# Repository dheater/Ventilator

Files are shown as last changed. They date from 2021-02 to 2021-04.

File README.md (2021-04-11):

# RespiraWorks Open Source Ventilator












This is a common repository for all hardware and software components of the RespiraWorks open source ventilator.

**If you intend to contribute, please read our [wiki](https://github.com/RespiraWorks/Ventilator/wiki).**

[RespiraWorks](https://respira.works/) is a 501(c)(3) non-profit organization with over 200 contributors worldwide
working to rapidly design a low-cost and [open-source](open_source.md) ventilator for communities underserved by the
global supply chain. Our objective is to provide the know-how and technology to enable others to manufacture these
systems and put them in the hands of those who need them most.

| Most recent rendering  | Assembled v0.3 prototype |
|:---:|:---:|
|  |  |

## Design Goals

We are dedicated to making this ventilator:
* [fully open source (software and hardware)](open_source.md)
* affordable (materials cost under US$2000)
* fully featured for extended clinical use through weaning and recovery
* vetted and filing-ready for regulatory review around the world
* optimized bill of materials to account for constrained (medical) supply chains
* designed for long-term clinical use beyond the pandemic

Most low-cost ventilator designs that have emerged in light of the COVID-19 crisis tackle the 'bridge' problem —
keeping a patient alive for 6-8 hours of closely monitored care until they can be transitioned to a full
ventilator. We are designing that full ventilator, a highly valued medical device critical to care beyond the
current crisis.

Our design shall provide essential features such as an intuitive, localized user interface, adaptive pressure- and
volume-based operating modes, fine control of oxygen concentration, High Flow Nasal Cannula and other advanced features.
What sets us apart from other similarly ambitious projects is our dedication to being fully open source. This repository
embodies that promise.

We are targeting middle- and low-income parts of the world that will deal with COVID-19 for longer, with less access
to healthcare, and a larger deficit of medical devices. We aim to deliver a design which meets the same operational
rigors of current commercial ventilators, while addressing the high barrier to entry for such devices.

The maturity of our design is attested to by our collaboration with [Foundry-M](http://www.foundrym.in/), a startup
in Visakhapatnam, India. We are working closely with our colleagues in India to adapt this design to their local
manufacturing capabilities and regulatory needs.

If you can lend your skills towards achieving this goal, please contact us at
[join-us@respira.works](mailto:join-us@respira.works?subject=[GitHub]%20Join%20request). A list of roles we are looking
to fill is also on our [website](https://respira.works/join-us).

## DISCLAIMERS

**This is an incomplete, as yet untested design that is not yet intended to be used on patients.**

**The repository contains live documents. There may be incomplete or contradictory information about various aspects
of the design. Components may or may not connect and integrate as intended. Contents may also be out of date. If you
decide to buy or build anything, do so at your own risk.**

## Repository Structure

* [**System Requirements**](https://respiraworks.github.io/Ventilator/system/system_requirements.html) -
  describes the requirement architecture, hierarchy, and process. Links to the releases of our system requirements,
  hardware specifications, and software requirements
* [**System Design**](design) -
  describes the functional implementation and design theory of the system
* [**Manufacturing Design**](manufacturing) - describes the physical design of the ventilator and its components.
  Includes CAD models and notes on the manufacturing process
* [**Main Circuit Board**](pcb) - design, materials, assembly instructions for the ventilator main circuit board
* [**Software**](software) - Source code for cycle controller and user interface, debug tools, test scripts, and test data
* [**Quality Assurance**](quality-assurance) - quality assurance strategy, testing plans, data

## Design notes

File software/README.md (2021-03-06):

# Ventilator Software

This directory contains the source code for the ventilator software, test code, sample data and debug utilities.

**DISCLAIMER: You should not use this on any living beings - as a ventilator, or in any other way.
These are utilities for bench with mechanical lung simulators only.
It is also assumed that you are familiar with the software architecture and generally know what you are doing.**

## Contents

* [design](design) - documents on software architecture and requirements
* [common](common) - code common to both controller and GUI executables
* [controller](controller) - code for pneumatic system controller (stm32)
* [gui](gui) - code for the ventilator graphical interface (Qt)
* [sample-data](sample-data) - sample data for offline testing and recorded performance test data
* [utils](utils) - scripts for debugging controller and mocking communications interface

## Quick start

If a proper enclosed unit is built as described under [manufacturing](../manufacturing),
it should be possible to deploy all GUI and controller software directly via the Raspberry pi that is integrated
into the ventilator unit.

Scripts for doing so are available under [utils/rpi_config](utils/rpi_config).

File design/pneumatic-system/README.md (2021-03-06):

# Pneumatic Design

**TODO:** Move stuff into subdirectories

**TODO:** Cross-link to manufacturing and other docs

## Physical Block Diagram

The figure below displays the physical pneumatic layout of the system.



## Control Block Diagram

### Rev 0.3 (Current)
- The current pneumatic control system (Ventilator Rev 0.3) is based on a single closed-loop pressure control around the patient pressure sensor, commanded by a state machine, with blower pinch valve, exhale pinch valve, and oxygen PSOL as actuators.
- Overall structure is OxygenLoop(PressureLoop(Actuator)).
- A flow sensor observes the combined air and oxygen flow to the patient and provides an estimation of the tidal volume.
- A slow outer loop controls the oxygen mix based on the O2 sensor.



### Rev 0.4 (Proposed)
- The proposed control starting with Ventilator Rev 0.4 adds a separate flow sensor for air and oxygen input.  Overall structure is Pressure Loop -> Flow Command -> Actuator. Flow becomes controlled instead of merely observed.
- Overall structure is OxygenLoop(PressureLoop(FlowLoop(Actuator))).
- Air and oxygen limbs will each have their own closed-loop flow controller, with the blower pinch valve and oxygen PSOL as actuators.
- The flow commands to these inner loops, as well as to the exhale pinch valve, come from an outer loop pressure controller which is closed around the patient pressure sensor.
- The pressure command to this outer loop comes from the state machine.
- FiO2 is controlled by a slow, outer-most control loop that changes the ratio of mixing between air and oxygen flow commands, and is closed around the oxygen sensor.



## Overview

Oxygen is supplied from an external pressurized source to the oxygen
port. Air is drawn in by the blower from the ambient room air.  The
device can also operate without an external supply of pressurized oxygen
in the event of supply shortages, (delivering only 21% FiO2).

### Air Path



Air is drawn in by the blower through a replaceable HEPA filter and
pressurized for use within the system. The blower maintains a relatively
constant speed and is open-loop controlled. The capability to  control
the fan speed to conserve power and increase response time has not been
incorporated in the current release. After leaving the fan, the
pressurized (5 kPa) air passes through a check valve included to prevent
oxygen backflow into the blower, as the blower is not rated for oxygen
duty and could present a fire risk. Following the check valve, a
proportional pinch valve regulates the downstream airflow. It does this by
adjusting the cross sectional area of the flow path in the tubing
built-in to the pinch-valve.

### Oxygen Path



The oxygen circuit is fed from an external oxygen source, with a
built-in regulator to step the pressure down to a pressure low enough to
allow it to be controlled by a 12V proportional solenoid (PSOL). The
design oxygen pressures at the inlet are 440 kPa - 120 kPa. The highest
pressure connection that is allowable is set by the capability of the
regulator, which cannot be used at a pressure higher than its rated
pressure. The minimum pressure is set by the orifice size in the PSOL.
With a supply pressure below the PSOL minimum, it cannot generate
sufficient flow to the patient.

A check valve prevents contamination of the hospital oxygen system.
Oxygen flow to the patient is controlled by the PSOL, whose orifice size
is controlled by a variable pulse-width signal. Currently, the PSOL is a
small automotive solenoid, which is not qualified for oxygen
duty, though it is functionally suitable
for development. Identifying a more reliable oxygen injection method is
a high priority for improving the design. It is the understanding of
RespiraWorks that the current PSOL is capable of being oxygen cleaned,
and it enables fine control and rapid development (assuming) they can be
sourced. As such, it has been included in the design.

### Oxygen and Air Mixing



The oxygen and air streams are mixed in the patient tubing without a
dedicated oxygen blender; instead, the oxygen blending function is
provided by proportional control of the two input streams. A galvanic
cell oxygen sensor is used to measure the oxygen content as the gasses
mix and provide feedback to the controller to calculate, display, and
enable closed-loop control of FiO2.

### In-flow Measurement



After mixing, the combined gasses pass through a venturi
differential-pressure flow sensor, where the flow rate of gas delivered
to the patient is measured. This gas passes a medical-grade anti-viral
filter upon exit from the machine for protection against viruses,
bacteria, or other foreign material. If these filters are not available,
the device also includes the capability to add an inline HEPA filter in
the panel mount for the tubing. This feature was included due to the
difficulty sourcing medical viral filters and the desire to support
additional options.

The patient circuit utilized by the ventilator is an ISO 5356-1 standard
22mm female dual limb circuit which interfaces to male ports on the
ventilator. If a humidifier, HME, or other device is used, these are
connected to the patient inhale or exhale circuit, as appropriate.

### Expiratory Limb

On the expiratory path, the exhaled gas returns to the ventilator via a
medical-grade anti-viral filter. This filter captures
droplets exhaled by the patient. This reduces the possibility of machine
contamination and dispersal of aerosolized virus from escaping into the
local environment. The expiratory flow rate is measured by a flow meter
similar to the one used on the supply side.

### PEEP Control



Following exhale flow measurement, another proportional pinch-valve is
used to set PEEP.

Air exiting the machine is processed through a final HEPA filter to
provide an additional safety factor for staff protection.

## Fan Selection

A key decision was made early on to use a blower (rather than a
pressurized oxygen source and control valve), to deliver patient air.



WS7040 fan with air intake assembly

The rationale for use of a blower in general, and this blower in
particular, had a few bases. First, using a blower (rather than
compressed air) allows the device to provide emergency ventilation with
only a relatively small power supply (around 50W continuous). This
allows the device to be portable and makes the device amenable to use in
field hospitals or mass casualty incidents where providing compressed
air or compressors can be challenging at scale. The blower selected is
also a common CPAP blower rather than a high performance ventilator
unit.

This allows the use of an easily achieved blower performance
specification, reduced cost and increased supply chain resilience.

However, selection of a CPAP blower does come with drawbacks—the blower
is not rated for oxygen duty and the pressure response of the blower is
slow, with a time constant some 1500 ms longer than comparable blowers
in ventilators. This led to the development of a high-flow, long-life
proportional valve, discussed in a subsequent section.

By placing oxygen mixing after the blower and using a check valve to
prevent backflow, the design ensures that the blower will never see high
oxygen concentrations.

Additionally, based on medical feedback, the delivered patient pressure
is no more than 60 cm H20. It is common for ventilators to specify
higher in order to ensure adequate ventilation for highly resistive
airways . Adopting this lower pressure spec allows the ventilator to
provide a pressure range that is most often needed, while avoiding
significant cost. It is compliant with 80601-2-12 and all specifications
reviewed for Covid-19 ventilators.

## Dual Limb Patient Circuit

The ventilator uses a dual limb patient connector (i.e., flow is sent to
the patient in one tube, and returns in a second). The flow is always
one way, starting from the device going to the patient, and returning in
a second limb. The other option is a single limb design, with an exhale
valve at the patient side.

A dual limb design was selected to allow for mechanical PEEP control, as
discussed in the next section.

Note as well that there is no check valve between the mixing volume and
the patient. Backflow is prevented through two means. First, there are
two check valves upstream of the tee, and no exhaust ports between the
tee and the patient, so gas can only flow back into the ventilator as
much as compressibility allows, which is not significant.
Second, even when fully closed, the
inhale proportional valve allows a small leakage (bias) flow through the
device, ensuring that, as long as the device is on, flow should never
enter the ventilator through the inhale port.

In a survey of suppliers, very low-cracking check valves (i.e. duckbill
valves) that were available in an inline configuration were not common.
The one that was tested had significant flow resonances at low
velocities which interfered with volume sensing. The present approach
uses no medical check valves. Normal (i.e., high-cracking) check valves
can be used on the air and oxygen lines.

## PEEP control

One of the differentiating features of the RespiraWorks pneumatic
circuit is the use of a controlled mechanical valve to maintain PEEP,
rather than a traditional passive PEEP valve. This decision was made
early on for several reasons. First and foremost, early in the pandemic,
PEEP valves were essentially unavailable and so they were not available
for prototyping, but also implied they might not be available for some
time. PEEP valves are effective, and so the option to design a new PEEP
valve, or base a valve on other open source designs was explored.
However, calibrating the spring constants proved to be a challenging
manufacturing process. Generally these types of passive PEEP valves are
considered disposable and so don’t experience long term use. This led to
concerns about long-term use of these PEEP valves as the spring
constants change with time/wear, motivating our incorporation of the
controlled solution.

Incorporating a controlled mechanical valve also provides the ability to
fully close the airway during inhale, thus preserving oxygen and
improving the response time of the inhale circuit.

Finally, the use of a controlled valve allows the device to adjust
settings based on user input, rather than requiring staff to
mechanically adjust the ventilator.

A fail-open valve also
prevents the need to include a separate valve for anti-asphyxia
protection, though this is still being evaluated with respect to the
hazard assessment..

The separate question has been raised of why not to use a pilot actuated
valve, either using patient pressure or a small proportional solenoid.
This was avoided entirely for sourcing considerations and was decided
early in the pandemic; this could be re-evaluated for future iterations.
In general, the pilot operated valves, such as those from Philips and
Galemed, were deemed a risk for countries without existing supply chains
to those manufacturers. The device seemed difficult to safely
re-engineer.

## Custom Proportional Pinch Valves

The design process for the entire ventilator started with a desire to
avoid custom components at all costs. However, after an exhaustive
search of valves, control methods, fans, and spare ventilator parts, it
was decided that a custom valve was the only option that would allow the
design to achieve targets on cost, supply chain, and features for
expiratory flow control. This decision was undertaken considering the
significant quality and qualification burden required for custom parts.

A rapid pressure swing on the inhale is required to provide ventilation
to low compliance lungs at a high respiratory rate, which was to that
point impossible using closed-loop control of the fan
alone.

The design originated by trying to tackle the PEEP problem as discussed
above. A design was specified in order to maintain a variety of
different PEEP levels and to avoid significant wasted flow during
inhale. In the process of development, it was realized that the same
design could also be used to provide a rapid pressure swing on the
inhale flow, in addition to exhale.


One of two pinch valves in each ventilator (early model)

The general operating principle of the pinch valve is to use a
high-torque stepper motor to rotate a cam/rotor onto peristaltic pump
tubing. The cam pinches the tubing against a platform affixed to the
base. Other than the interior tubing, the valve assembly never comes
into contact with the gas stream. The highest wear portion of the design
is the tubing itself, which can be replaced for less than 1 USD when it
must be replaced.

One option explored, not currently implemented, is to
provision the device and arrange the components with an extra length of
tubing (not shown above) such that it can be fed through the valve over
time; pushing the extra from upstream to downstream of the valve and
changing the wear point. This maintenance operation will extend valve
lifetime significantly and should be able to be performed by hospital
staff in addition to maintenance technicians.

Life-leader testing is currently underway to demonstrate the ultimate lifetime of
the valve; though it will take time to accumulate. As of submission of
this proposal, the valve has been running at a 200% duty cycle for 21
days continuously. Further information on life leader testing can be
found in the 01-02 Progress Status Update.

An additional advantageous feature is that the valve is closed through a
stepper motor which does not maintain its state when power is lost. The
elastic modulus of the tubing, coupled with the fact that the rotor can
not reach a "locked" position is sufficient to force the valve open if
the power fails—the
valve is normally open, and allows the exhale valve to also function as
an anti-asphyxia pathway.

The pinch valve itself is built from relatively simple components,
discussed in more detail in 05-01 05-01 Production Methods for Custom
Components.

## Proportional Solenoid

Proportional solenoids (PSOLs) are used in many applications (including
other ventilators) for precise, rapid control of high pressure gases.
The major factor arguing against the use of a PSOL in the RespiraWorks
ventilator is that PSOLs with applicable characteristics are, almost by
definition, produced for ventilator use, with an associated limitation
on cost and availability. While some are available outside this market,
those are typically not designed for use with high-pressure oxygen. High
pressure oxygen requires real safety considerations, as the opportunity
for fires can occur from improper lubricants, components, or errant
sparks.

All that said, from the options considered and reviewed, a properly
designed and sourced proportional solenoid is the cheapest, most
reliable method for controlling high pressure gas flows, provided the
flow rates and pressures are modest. There is still interest in
improving the oxygen circuit to use a high-pressure rated pinch valve,
perhaps in combination with a 2-way (rather than proportional) solenoid
as part of a future cost optimization.

In the near term, a proportional solenoid was selected in order to
facilitate development rather than tackle the high-pressure pinch valve
design.

A secondary but important consideration is that in order to protect the
patient from barotrauma, it is important for the oxygen valve to fail
closed when power is lost, which is a feature of the selected
proportional solenoid but not of the pinch valve.

## Venturi-Based Flow Sensing

One of the guiding principles of our design was to avoid using
proprietary equipment and avoid disposables associated with each
patient. This philosophy led us to develop a custom venturi-based flow
sensor. It lacks some low-order accuracy, leading to reduced tidal
volume accuracy, though still within spec. In return, by producing an
easy-to-sterilize sensor the device can avoid proprietary and costly
proximal flow sensors.



A venturi flow sensor with a differential pressure sensor used to
calculate flow

Venturi flow meters are commonly used to measure the flow of gasses by
measuring the change in pressure of the gas as the area is constrained.
Relative to other sensor types, a venturi is the cheapest method for
measuring flow rate, as it produces the largest signal to pressure drop
ratio of any flow measurement solution.

RespiraWorks initially pursued numerous different flow measurement
methods, including pneumatic methods such as pitot, pneumotachograph, or
orificing flow sensors, which all require far more sensitive (and
expensive) pressure sensors than a venturi. RespiraWorks also reviewed
existing thermal mass flow sensors, which were not available during
initial development. While they are costly, thermal mass sensors provide
better low-noise signals at low flow rates and may in the long run prove
to be a more reliable and robust solution. The issues with the sensor
led to significant effort on software algorithms to improve the
response. The effort that went into robust volume and flow integration
will make it relatively easy to change to a different (better) sensor,
but testing has shown the accuracy sufficient to control flow rate and
estimate tidal volume within required accuracy.

For our ventilator, we designed venturis that can measure the high flow
required, but that can also be made through widespread, low cost
manufacturing processes (e.g. injection molding).

The venturi design was based around a garden fertilizer injector.
 Though all initial prototypes have been 3D printed, the required
geometry is almost identical to a ½" garden venturi, which can be
purchased at quantity for 2-4 USD / pc.

Venturis produce a large signal ratio.  In ours, a maximum pressure drop
of 5cm at 100 slpm produces a measured signal of 4 kPa, which can be
measured with cheap, widely-available automotive differential pressure
(dP) transducers.

In contrast, similar flow orifice and pneumotachograph style sensors
require expensive amplified pressure sensors to measure signals in the
range of just 100 Pa.

These dP measurements can then be converted into flow rate estimates
based on the physics of the venturi. By placing one venturi on the
inhale limb and one on the exhale limb, the flow rate going to the
patient is estimated by subtracting the two flow measurements.

## Oxygen Sensing

Based on conversations with doctors, there were two driving constraints
for our oxygen sensing needs. First, the ventilator needed to be able to
provide fine FiO2 control, not just a few set-points. Second, the
ventilator needed to work with oxygen tanks and concentrators that were
not actually 100% oxygen (e.g., improperly charged hospital oxygen
tanks), since reliably pure O2 can be unavailable in many developing
markets.

Based on both of these constraints, we needed an oxygen sensor to
measure the actual oxygen content of the flow. We chose a galvanic
oxygen sensor because they are widely available.

A downside of galvanic O2 sensors is their finite lifetimes. Therefore,
we will likely add an ability to also measure oxygen flow rate, so the
system is more robust to a failure of the oxygen sensor (and can sound
an alarm that maintenance is required). We’re exploring whether a sensor
that uses fluorescence quenching can provide the requisite sensitivity
and responsiveness, as this would last for the lifetime of the device.

## Filtration Approach

Filtration is critical to both keeping the ventilator from being
contaminated by the patient or the environment, and keeping the patient
protected if the ventilator does become contaminated.

In our system this is accomplished by dual filtering on both the inlet
and exhale paths, such that for each path, there is a filter between
both the ventilator and the patient and the ventilator and the
environment.

HEPA filters were chosen because they are widely available and designed
to filter both large and small particles. The HEPA filters are held in a
custom enclosure that is designed to be injection molded.  It’s easy to
disassemble, clean, and reassemble, making it easy to change filters
over time.

## Overpressure Protection

To date, RespiraWorks has not been able to identify a robust, reliable
method for overpressure relief. Numerous options have been tested. All
of these present failure modes, or had leakage issues which were likely
more significant than their pressure protection function. One valve was
identified which worked well, but the price was over \$100 per valve.
The current design does not possess a dedicated overpressure protection
relief valve. The fan specification is such that it likely cannot result
in a pressure greater than 55 cm H2O. However, the PSOL can easily
generate pressures in excess of 60 cm H2O. There is some leakage at high
pressure through the pinch valve, which is pressure dependent but this
is likely not sufficient for patient protection. Additionally, most
failure modes identified for the ventilator result in the PSOL failing
closed; However, this is not sufficient from a risk consequence
perspective, and this is an area requiring further address.

## Anti-Asphyxia Protection

The device currently does not have a dedicated anti-asphyxia protection
valve. Requirements on flow and flow resistance for anti-asphyxia have
been included in 01-3 System Requirements. The current anti-asphyxia
strategy in the event of ventilator failure is to actuate alarms (see
Software) section and to fail-open the exhale control valve, which
should provide an inhalation and exhalation pathway. It has not been
evaluated if this pathway meets the flow resistance requirements
identified, nor if this failure mode is appropriately addressed from a
hazards perspective.

## Planned Mechanical Upgrades

The RespiraWorks ventilator has developed organically over time. As the
design matures, a number of upgrades are under consideration beyond the
current design.

These include:

-   Adding a pressure transducer prior to the patient inspiratory limb
    (either in addition to the one on the exhale venturi or replacing
    it). The benefit of placing the pressure transducer here is that if
    something happens to the line between the patient and the exhale
    portion of the ventilator (e.g. it is stepped on), the ventilator
    can detect such an obstruction and maintain basic safety.
-   As mentioned above, adding flow sensing on the oxygen inlet circuit,
    to aid in FiO2 control and make the system more robust to failure of
    the oxygen sensor.
-   Adding redundant pressure differential sensors to make it easier to
    detect a sensor failure.

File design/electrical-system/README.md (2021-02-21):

# Electrical Design

**TODO:** update electrical circuit diagram to reflect current design



The electronics system provides power to the ventilator, real-time
control of its sensors and actuators, safety protections and alarms, and
a user interface for delivering information and controlling the
parameters of its operation.

As with the pneumatics system, the electrical system is designed to be
amenable to global supply chains, be low cost, and yet be robust and
reliable.

## Computing Architecture

A dual-computer architecture was selected.  There is a Cycle Controller
based on STM32 that handles the real-time control of the ventilator’s
sensors and actuators.  Connected to this is a UI Computer based on a
Touchscreen, Raspberry Pi 4, and Linux to provide the user interface.
 This design allows us to delegate the most critical functions to a
simple design that can be reasonably reviewed and tested in its
entirety, while also allowing enough complexity in the UI Computer to
provide a comprehensive user interface.



The division of responsibility between the two computing elements is
divided roughly by the immediacy of a potential failure.  For the class
of operations in which a potential failure could result in a hazard too
quickly for reasonable human intervention, the Cycle Controller is used.
 For the class of operations in which a potential failure can reasonably
be addressed by human interaction in a reasonable amount of time given a
timely alarm, the UI Computer is used.  This design also allows for
self-checking between the two computing elements to mitigate
single-point failures.

The STM32 microcontroller was selected because it is more powerful than
Arduinos or similar popular microcontrollers, but it is still cheap,
widely available, well-documented, and has extensive debugging tools.
The STM32 is proven to be a reliable medical electrical component and
has a diverse I/O set for pneumatic and mechanical control.  The
operation of the Cycle Controller is kept as simple as possible to
facilitate comprehensive review, test, and verification of its function.

The Raspberry Pi was selected as the UI controller for its wide
compatibility with existing human-machine interfaces and robustness to
supply chain shock. The Raspberry Pi also enables rapid software and UI
development by supporting a Linux-based operating system and the common
HDMI interface. It supports remote monitoring, as well as automated
testing, through its wired and wireless network interfaces.  While
powerful and flexible, the complexity of its operating system means that
real-time control cannot be sufficiently guaranteed or verified.  Hence
all time-critical operations, such as ventilator pneumatic control, are
handled by the STM32.

A serial communication link using checksums to ensure data integrity
provides reliable communication of settings and data between the two
computing elements.

Each computing element has its own alarm system as well as a watchdog
timer.  If either computing element becomes non-responsive, the
watchdogs will put it into a safe state and restart it.  The UI Computer
monitors the Cycle Controller and vice versa, and will issue an alarm if
the other stops responding.  Each controller can trigger an audible
alarm system independently, and the UI controller can display alarms
visually as well.  The motherboard features bright LEDs in 3 colors to
provide visual alarms independently of the touchscreen interface.  The
Cycle Controller and UI Computer each have independent control of their
own set of bright red, yellow, and green LEDs.  Due to an error in the
motherboard design, the Cycle Controller only has command of the red LED
in its set.  This will be fixed in a future revision.

A custom motherboard has been designed to host both the UI Computer and
Cycle Controller, as well as all the required communication, filtering,
safety protections, sensors, motor drivers, and power supplies.  This
improves both the manufacturing assembly and the electromagnetic
immunity of the electronics.



All mainboard design files are maintained in this repository
in the [../../pcb](../../pcb) directory.

Wiring materials and assembly guide on [this page](../../manufacturing/wiring).

## Closed-Loop Pneumatic Control

All key elements of the pneumatic system are controlled by electronics.
The WS7040 blower features its own driver, which is powered by 12VDC
controlled by the motherboard with a PWM signal. The
RespiraWorks-designed proportional pinch valves are driven by stepper
motors, which are controlled by powerSTEP01 stepper driver ICs. The
powerSTEP01 is available in a daughterboard compatible with the STM32
developer module - this synergy enables rapid hardware and software
development around controlling airflow, and provides a proven electronic
design for integration into the next motherboard revision.

The differential pressure (dP) sensors that monitor inhale/exhale flow
rates are board mounted as well. These are automotive differential
pressure sensors which are cheap and widely available in large
quantities worldwide.  They monitor the pressure difference across the
two venturi-based flow sensors as well as the delivered patient
pressure.  They output an analog electrical signal which is filtered and
conditioned on the motherboard and delivered to the STM32 Cycle
Controller.  They are pneumatically connected to the venturis by 2.5mm
flex tubing.  In the case of the single-ended pressure measurements only
one of the two pressure ports is connected by 2.5mm tubing, and the
second port is referenced to atmospheric pressure.

The oxygen supply is controlled by a proportional solenoid.  The
motherboard features two high-current MOSFET switches fused with
resettable thermal fuses and protected by flyback diodes for operating
inductive loads.  These switches are capable of fixed on/off control or
proportional PWM control of a 12V load.  One of these switch channels is
used for the proportional solenoid.  The other channel is uncommitted
and can be used for a future feature, such as humidifier heating
control.

For future expansion of features, the motherboard also provides 4
powered I2C ports that can be configured for 3.3V or 5V operation.
 These can be used to command actuators, read sensors, or interface with
other supporting devices such as an external humidifier or
uninterruptible power supply (UPS).

## Power Supply Design

An early decision during the electronics design was to standardize the
input voltage to 12 VDC. This enabled rapid prototyping around the
WS7040 blower and driver. Using 12VDC enables the use of
widely-available sealed lead-acid security system batteries or
automotive batteries as a backup or primary power source in field
hospitals. 12VDC is also a common battery standard and there exist
60601-1 compatible wall adapters for operation in a more conventional
medical facility.

The custom motherboard features DC/DC converters to supply and regulate
the logic voltages for the on-board electronics.  In the next iteration
of the motherboard, backup batteries shall be present for supplying
emergency shutdown alarms (when both mains and backup battery are absent
or depleted) as well as providing real-time clock support for
monitoring, diagnostics and logs.

## Human-machine Interface

A 7-inch capacitive touchscreen is selected as the primary user
interface. This is a color display capable of receiving user input and
refreshing data with 50 ms latency.  Both the display and the integrated
speakers are operated through the HDMI interface of the UI controller.

The cycle controller has access to its own dedicated audio system. This
is a simpler piezo buzzer, driven by a square wave signal and capable of
the required output volume. The buzzer and LEDs provide a secondary
emergency interface in the event of a touchscreen failure.

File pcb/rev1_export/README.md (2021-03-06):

# RespiraWorks Ventilator Mainboard Rev 1.0 

This directory contains the PCB design files exported from Altium and instructions for setting up the PCB for operation. 

The snapshot for this file is **20200424v2-RELEASE-CANDIDATE-2**.

Previous versions of this iteration are found in the repository up through
[commit 2513e5d](https://github.com/RespiraWorks/Ventilator/commit/2513e5da6fe3e8d02f5f1c38cb00bee6b4fabf3e).

## Contents:

The complete turn-key manufacturing files for Rev 1.0 are provided here. This package includes PCB artwork files, NC 
drill data, fabrication and assembly drawings, Bill of Materials, and machine-assembly centroid (pick-and-place) files.
Any standard PCB fabrication and assembly vendor will be able to manufacture these boards using the provided files.

**[Turnkey Manufacturing Package](20200424v2-RespiraWorks-Ventilator-Rev1.0-RC2-PKG-TURNKEY.zip)**

This package includes everything required to fabricate and assemble the Rev 1.0 PCB:
- Gerber Files
- NC Drill File
- BOM (Bill of Materials)
- OPL Substitution BOM for SeeedFusion PCB vendor
- Pick and Place File
- Assembly and Fab Drawings
- IPC Testpoint File

**[Schematic](20200424v2-RespiraWorks-Ventilator-Rev1.0-RC2-DWG-SCH.PDF)**

**[Electrical Hardware Requirements and PCB Interface Control Document](https://docs.google.com/spreadsheets/d/1JOSQKxkQxXJ6MCMDI9PwUQ6kiuGdujR4D6EJN9u2LWg/edit?usp=sharing)**

**[3D STEP file](20200424v2-RespiraWorks-Ventilator-Rev1.0-RC2-3D-STEP.step)**

**[Complete Altium Design Project Files](20200424v2-RespiraWorks-Ventilator-Rev1.0-RC2-PKG-DESIGN.zip)**

**[Fabrication Drawing](20200424v2-RespiraWorks-Ventilator-Rev1.0-RC2-DWG-FAB.PDF)**

**[Assembly Drawing](20200424v2-RespiraWorks-Ventilator-Rev1.0-RC2-DWG-ASSY.PDF)**

**[Bill of Materials](20200424v2-RespiraWorks-Ventilator-Rev1.0-RC2-ASSY-BOM.xls)**

**[Simplified STEP file without STM32 or Rpi](20200424v2-RespiraWorks-Ventilator-Rev1.0-RC2-3D-STEP-NO-PI-NO-STM.step)**

## Requesting hardware for development

If you are a RespiraWorks contributor, request dev hardware by making an entry
[here](https://docs.google.com/spreadsheets/d/1rf-cOTlQL_LnzrZq-64n7_R_pFyFMdCAxsPC65YqKUg/edit?usp=sharing)

## Important Rev 1.0 PCB Errata
* [#739](https://github.com/RespiraWorks/Ventilator/issues/739): DNP resistors populated on board, typing 3.3V to the 5V
  rail (bad) - if you have SN 01, 02, 03, or 05 - don't continue using the board without executing the fix in this issue
  ticket.  See ticket for rework instructions and photos.  All other serial number boards are shipping with this issue
  fixed.
* [#738](https://github.com/RespiraWorks/Ventilator/issues/738): Yellow and Green alarm LEDs don't work due to a pin use
  conflict on the nucleo
* [#745](https://github.com/RespiraWorks/Ventilator/issues/745): Blower command is 5V but nucleo outputs 3.3V.  All
  boards are currently shipping with a level translator fitted which addresses this problem, however the blower will
  turn on full blast briefly at reset.  See ticket [#745](https://github.com/RespiraWorks/Ventilator/issues/745) for rework instructions. ([#740](https://github.com/RespiraWorks/Ventilator/issues/740) - to be fixed in
  next rev)
* [#736](https://github.com/RespiraWorks/Ventilator/issues/736) I2C sensor connectors labeled A, C, B, D. Should be A,
  B, C, D :facepalm:  To be clear, what this means is, the I2C multiplexer assignments, as labeled on the board in Rev
  1.0 are: MUX0: SENSOR A; MUX1: SENSOR C; MUX2: SENSOR B, MUX3: SENSOR D
* [#846](https://github.com/RespiraWorks/Ventilator/issues/846): anti-miller caps C33 and C34 filter out PWM signal and
  prevent proper operation.  The Miller effect is only present at startup and doesn't cause a problem with permanently
  connected loads like the PSOL.  Remove C33 and C34.

## Rev 1.0 PCB Quick Start Guide for Electrical Developers
* If you are building a complete enclosed ventilator, follow the instructions on [display_panel](../../manufacturing/internals/display_panel/README.md).
* If you have SN 01, 02, 03, or 05, make sure you check the errata above before you proceed or you may damage the Rpi.
* If you intend to use the stepper motor-based pinch valves, you will need to solder some wires to power the stepper
  driver as it takes a power input for the motor that is separate  from the logic power it gets from the Nucleo below.
  We will piggyback off the blower driver power socket.  Solder two 20cm wires of 22awg or thicker to the backside of
  J10, the blower power connector. The square pin pad is negative.

solder power connection
* Verify that you have an STM32-L452RE module (not an STM32-L452RE-P module, they have different pinouts - see #51)

verify model
* Plug the Nucleo into the PCB, observing the silkscreen (white outline on the board) for correct orientation.

plug in the nucleo
* Move the JP5 jumper in the upper-middle-center of the Nucleo board to the E5V position.  This tells the board to
  expect external power from the PCB.  This will avoid programming problems.  If you wish to remove the Nucleo board
  and work with it on its own without the PCB, move the jumper back to the U5V position to power it from USB.

plug in the nucleo
* If you have a X-NUCLEO-IHM03A1 or X-NUCLEO-IHM02A1 stepper driver accesory, plug that in on top of the Nucleo.  The
  long gold pins of this module can get bent so make sure they are straight and they all go into their respective
  sockets successfully.  The stepper driver green connectors go in the direction of the white connectors on the
  mainboard PCB.  For setting up multiple stepper boards and/or connecting actual steppers, see
  [this guide](../../manufacturing/internals/display_panel/electronics/stepper_drivers).

plug in the stepper driver
* If you are using an Rpi 3B+ or 4 with this PCB, plug this into the RPI socket.  Note that if you have the standoffs
  fitted, do not overtighen them as this can damage the Pi.

plug in the Rpi
* If you are using Touchscreen w/ Speakers with your Rpi, connect an HDMI cable (included with Touchscreen package)
  between the Pi and the Touchscreen.  Similarly, connect a USB micro cable (included with Touchscreen package) between
  the Pi and the TOUCH+5V connector on the Touchscreen.

plug in the Touchscreen
* If you are connecting a blower, take the 6-pin to 6-pin JST XH cable and connect it between the BLOWER CTRL connector
  at the top of the PCB with corresponding connector on the blower driver.  Likewise, take the 2-pin to 2-pin JST VH
  cable and connect it between BLOWER POWER connector at the top of the PCB and the corresponding connector on the
  blower driver.

plug in the nucleo
* The PCB must be powered in order for the Nucleo to program correctly.  A power cable which plugs into the upper left
  corner of the PCB is provided with the board and allows it to be powered from any 12V, 1.2A or greater power adapter
  with a 5.5x2.1mm center-positive barrel jack.  You will want 5A or more if you are also powering solenoids, blowers,
  and heaters from the PCB.  Plug this in to the power the board.  A green POWER light in the upper left of the PCB
  should come on, and the various status lights of the Rpi and Nucleo will probably also come on.

plug in the nucleo
* When programming over the Nucleo USB interface, the board emulates an ST-Link programming the MCU over SWD.  Use these
  settings in the toolchain of your choice.
* The bringup code was written in the Arduino IDE environment with STM32duino installed and can be found here along with
  basic instructions for setting up STM32dino and programming the STM32. (disclaimer: this code is not part of the
  project and is pretty much unsupported, use at your own risk.  The listing of hardware pin #defines at the top might
  be useful): [pcbreathe-bringup](https://github.com/inceptionev/pcbreathe-bringup)
    * for more test code with a state machine for running a ventilator setup in closed-loop control mode,
      see this repo: [FMLtest](https://github.com/inceptionev/FMLtest)
* The main reference for pin and GPIO assignments on this board are in the
  [Electrical Hardware Requirements and PCB Interface Control Document](https://docs.google.com/spreadsheets/d/1JOSQKxkQxXJ6MCMDI9PwUQ6kiuGdujR4D6EJN9u2LWg/edit?usp=sharing)
* The large power connectors on the PCB are JST VH type.
* The smaller peripheral connectors on the PCB are JST XH type.
* The buzzer requires an oscillating signal to make sound, it is designed for peak output at 2.4kHz.  Take off the
  kapton cover at your own hearing risk.
* On the MPXV5004DP differential pressure sensors, the upper port is the positive measurement, and the lower port is the
  negative.  The transfer function, assuming a 12-bit ADC, is P[kpa] = ADCcounts/819 - 1
* The switched heater and solenoid outputs can support a resistive or inductive load up to 2A.  Refer to schematic for
  pinouts.
* The i2c sensor connectors are initially configured for providing 3.3V supply power to the sensors, but can be
  configured for 5V.  Each sensor can have its own voltage; they do not need to be the same.  If you need to switch to
  5V, see the schematic for the resistors to change.  Refer to schematic for pinouts.
* The analog pressure sensors have an anti-aliasing filter value of 100Hz.

## Stepper driver setup

When the PCB was originally designed, the ability to add a stepper driver was essentially a hedge, a backup *just in
case* we wanted to try something that required a stepper motor.

To use stepper motors, you must add stepper driver boards as described in
[this guide](../../manufacturing/internals/display_panel/electronics/stepper_drivers).

## System integration

The PCB and its daughter-boards are part of the
[electronics sub-assembly](../../manufacturing/internals/display_panel/electronics).

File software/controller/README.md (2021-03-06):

# Ventilator controller software

Here resides the code for the ventilator controller.

Please also see the [Software design pages](../design/controller_architecture.md) for more information on controller architecture.

## Rationale and structure

The ventilator actuators must be driven by control loops ensuring continuous
breathing according to doctor-provided parameters, while also ensuring
no harm is done to the patient.

Controller code is separated from the user interface code. This makes the code base
smaller, easier to maintain, and lessens the risk of unexpected behavior.

The controller shares the [common communications code](../common) with the GUI.
The part of the code specific to the controller resides here.

**Directories:**
* [lib](lib) - most of the substantive controller code, must all be libraries to be unit-testable by platformio
* [test](test) - unit tests
* [integration_tests](integration_tests) - code for (semi-)automated hardware-in-the-loop testbeds
* [platformio](platformio) - build configurations and deployment scripts
* [src](src) - just the main loop for controller
* [src_test](src_test) - just the main loop for unit tests

**Files:**
* [platfomio.ini](platformio.ini) - the equivalent of a "make file" which governs how platformio builds targets
* [coverage.sh](coverage.sh) - script for generating unit test code coverage reports
* [controller.sh](controller.sh) - general utility script for:
  * building controller firmware
  * running unit tests
  * running static checks
  * uploading/deploying firmware
  * self documented if you run it without parameters...

## Development toolchain

The target platform for this code is the STM32 processor (currently, the Nucleo L452RE to be precise).

We use [platformio](https://platformio.org/) for building the controller code.
Platformio has a CLI and an IDE. You'll need the platformio CLI in order to build
from the command-line, even if you also install the IDE.

Instructions for installing:
 * [CLI](https://docs.platformio.org/en/latest/core/installation.html#super-quick-mac-linux)
 * [IDE](https://docs.platformio.org/en/latest/integration/ide/vscode.html#installation)

Note that an issue prevents platformio CLI 5.0 and 5.0.1 to run our unit tests. If you are using one of these versions, you will need to upgrade to 5.0.2 or newer version using:
```
$ platformio upgrade
```

Here's a [video introduction](https://www.youtube.com/watch?v=EIkGTwLOD7o) to platformio.

PlatformIO works on Windows as well.
You'll need to install [Atom](https://atom.io/),
[Clang+LLVM](https://releases.llvm.org/download.html),
and [Python](https://www.python.org/downloads/windows/).
(Note: you may be asked to install Python 2.7, but PlatformIO works with Python 3.5+ as well, ostensibly.)

You also need to install the package `libtinfo5` on Linux. Clang-tidy needs this package to run its checks,
but platformio will just say all checks have passed without giving an error if it's missing.

## Building and testing

After installing platformio, you should be able to build and test as follows.

```
$ ./test.sh
# This will run a few commands, such as "platformio run" and
# "platformio test -e native".
```

This is the same script that runs on our continuous integration server (Travis CI).
Run it frequently during development to catch errors/style violations early.

Sometimes PlatformIO can get into a bad state -
e.g. if things don't build for you in `master`, try:

```
$ rm -rf .pio/
```

## Running on the controller

To run this you will need at a Nucleo dev board and/or some version of the PCB.
For various builds of the physical system, please refer to the [manufacturing](../../manufacturing)
section in this repository.

Plug in the STM32 to your machine, then ask platformio to list all devices connected.
You should see a USB serial port corresponding to your device.

```
$ pio device list
/dev/cu.usbserial-14220
-----------------------
Hardware ID: USB VID:PID=1A86:7523 LOCATION=20-2.2
Description: USB2.0-Serial
```

Now you can build and upload to the device.
**Note:** The following command should be run in this directory (same as where `platformnio.ini` lives).

```
$ pio run -t upload
```

A more convenient way to run is to use the `./controller.sh --run`. If you have multiple Nucleos that you
want to deploy to, you should consult the [platformio configuration guide](platformio).

### USB permission problems

If `pio device list` did not show the Nucleo as, for example, when attempting to deploy directly from the Raspberry Pi,
you may have to give yourself rw permission on the USB device.

Find the device ID with `lsusb`. Let us assume in this case, that it shows
`Bus 001 Device 004: ID 0483:374b STMicroelectronics ST-LINK/V2.1`.

Add a udev rule for that device that mounts it with 666 permission. For example, create a file
`/etc/udev/rules.d/99-openocd.rules` with the following line:

```
ATTRS{idVendor}=="0483", ATTRS{idProduct}=="374b", MODE="666"
```

After that, either you unplug and re-plug the USB for STM32 or you restart the pi, you should see something like this:

```
pi@raspberrypi:~ $ pio device list
/dev/ttyACM0
------------
Hardware ID: USB VID:PID=0483:374B SER=0663FF303435554157115746 LOCATION=1-1.4:1.2
Description: STM32 STLink - ST-Link VCP Ctrl
/dev/ttyAMA0
------------
Hardware ID: fe201000.serial
Description: ttyAMA0
```

### Other udev problems

If you get the following error, it means platformio was unable to find a connected device.

```
# This means pio couldn't find a device to upload to.  Check that it's connected?
Error: Please specify `upload_port` for environment or use global `--upload-port` option.
```

You may have to modify your `udev` rule to enable flashing of the controller as follows:

```
curl -fsSL https://raw.githubusercontent.com/platformio/platformio-core/master/scripts/99-platformio-udev.rules | sudo tee /etc/udev/rules.d/99-platformio-udev.rules
sudo service udev restart
sudo usermod -a -G dialout $USER
sudo usermod -a -G plugdev $USER
```
and then either re-login or restart machine.

For more details on this, see the following articles:
[platformio FAQ](https://docs.platformio.org/en/latest/faq.html#platformio-udev-rules)
[community forums](https://community.platformio.org/t/stm32-vs-code-mbed-upload-issue-error-libusb-open-failed-with-libusb-error-access-error-open-failed/10650)

Alternatively, you can upload the firmware.elf and firmware.bin files to the controller mounted as a USB storage device.

## Testing with hardware

Some (semi-)automated integration tests are in the [integration_tests](integration_tests) directory.

Debug interface and manual testing utilities are in the [../utils](../utils) directory.

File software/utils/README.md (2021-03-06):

# Utilities

## Raspberry pi deployment scripts

If a proper enclosed unit is built as described under [manufacturing](../../manufacturing),
it should be possible to deploy all GUI and controller software directly via the Raspberry pi that is integrated
into the ventilator unit.

Scripts for doing so are available under [rpi_config](rpi_config).

## controller_debug

[controller_debug.py](controller_debug.py)

This Python script can be used to interface with the controller via the virtual serial
port that is created when the USB cable to the Nucleo board is plugged in.

There is a [brief tutorial](controller_debug.md) on how to use it.

This interface is the basis for automated performance tests, such as [run_covent_tests.py](run_covent_tests.py).

## decoder

[decoder.py](decoder.py)

This is a decoder of serial packets sent from controller to GUI.

## DMA UART test

[dma_uart_test.py](dma_uart_test.py)

This is an integration test. Test code is deployed to the
controller, and a python script is run locally to confirm that the controller
is running as expected and not resetting.

The controller test code is [here](../controller/src_test).

It is deployed like this:
```bash
pio run -e stm32-test --target upload
```

Then you can run:
```bash
python dma_uart_test.py
```

## Regenerating python proto bindings

*The Python proto bindings really ought to live in common/, next to the .proto
file and the generated C++ code.*

On my Mac, the following works to regenerate the Python proto bindings.

```bash
( cd $(git rev-parse --show-toplevel) && \
  protoc -I/usr/local/Cellar/nanopb-generator/0.4.1_1/libexec/proto \
         -Icommon/generated_libs/network_protocol \
         --python_out=utils \
         common/generated_libs/network_protocol/network_protocol.proto )
```

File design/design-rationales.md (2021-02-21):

# Design Rationales

NOTE: The documentation below is a summary and may be out of date.

## Overview

This file is meant to document the rationales for the design decisions we're making - or things we considered and rejected.

Caution: this document has not been formally reviewed and is a work in progress. Be responsible to
understand the provenance of documentation.

Also note: right now we are collecting initial information here since it is easier - we may split
this up to have the different sections live with the different component folders, but we'll figure that out later.

## Guiding Principles

1. **Low cost but robust and safe** - we want to create something that is affordable, but also that can perform the
necessary duties reliably with high confidence over extended periods of time. The goal is to satisfy external
specifications for ventilator requirements - but also assess the cost of the requirements and not blindly follow them if
it drives big decisions in the system.

2. **Keep It Simple (Stupid)** - remove complexity wherever possible to reduce failure modes (and cost), without
sacrificing key functionality (though certain functionality may not be achieved)

3. **Make it something that doctors will use** - it won't necessarily do everything, but we want the ventilator to
provide the key needs of doctors. Therefore, we must keep doctors extremely in the loop and constantly get feedback from
them on what we're doing.

4. **Amenable to developing world supply chains and maintenance** - don't presume that the medical context we might be
used to is the same in our target market. The only way to get this information is contact with doctors and workers
familiar with the facts on the ground.

5. **Open source** - we want this project to be something that anyone who wants can build off of and leverage.
Therefore, all designs, rationales behind those designs, requirements, processes, etc. will be documented in a common
repo that everyone has access to. **#TODO** - go through and make sure all of the links in here are in git so that
people can access them (some slack links exist temporarily before the information is fully resolved and moved to git).

## System CONOPS/System Design

More detailed thoughts on this [here](conop.md).

* Targeting **pressure control** for two reasons:
    1. We got early feedback that this was most important to doctors - though we have gotten feedback that volume
       control is also important.
    2. A lower cost pressure controlled system seemed more achievable - and theoretically a good pressure controlled
       system should be able to do volume control. Currently we are pursuing pressure control and will be evaluating how
       accurate volume measurements we can get to determine if the design can also support volume control.

* **Doctors need fine control of FiO2** -> this drives the need for an oxygen supply, the need to support oxygen mixing
and sensing, and the need for a variable state valve on the O2 supply to adjust the flow rate dynamically.
**#TODO** Need more info on the ox system design we pick.

* **Multiple closed loop (feedback control) systems create complexity by creating interacting dynamics** -> we're
attempting to only have a single closed loop controlled part of the system at a time and to target one key feature (e.g.
pressure with FiO2 achieved across cycles). We're also working to determine which components (e.g., valves, blower) need
to be controlled and how in order to figure out what will actually support the system requirements.

* Anything that will be exposed to high oxygen concentrations and pressures needs to be safe and ox-clean. This drives a
desire to **reduce the number of items directly in the flow as much as possible**, especially for high-pressure (greater
than 1 bar O2)

* **Air valve after the fan/blower with air valve being closed loop controlled and fan being open loop** -> The
ventilator requires a high rise time of the pressure when transition from PEEP to PIP. A motor which can change the fan
inertia this quickly against increasing pressure ends up being the fan for some high-performance ventilators, or
expensive. We have solved this by the use of a proportional valve after the fan. The fan runs at constant power, and the
pinch valve is used to modulate the flow. For reference, one fan we got quoted was $500 and we were never able to get one
delivered. A fan capable of meeting the pressure spec + an air valve capable of the rise time spec was less than $75.

* The goal is to maintain **some bias flow through the system at all times**, both to help the fan and to avoid big
surges from completely opening and closing different parts of the circuit. This also helps ensure a 'one way' flow of
particles and aids with sterilization.

* **Trigger breath transitions off of changes in flow instead of pressure** -> Because the ventilator is pressure
controlled, it adapts to small changes in pressure by adjusting the flow rate (by adjusting the valve states) in order
to maintain pressure. Therefore, changes in flow rate are a better sign that the patient is attempting to inhale or
exhale. **#TODO** need to confirm this/flesh this out as we go

* **Anti-asphyxiation design** (**#TODO** need to confirm all this)
    * **Pneumatic** If the ventilator loses power, it is important that the patient is able to breathe and is not given
      dangerous amounts of pressure/flow. The oxygen system is fed by an external pressure source that the ventilator
      doesn't control; therefore, in the loss of power it is important to shut off flow from the oxygen system to keep
      the patient safe. We accomplish this by using a normally closed solenoid on the oxygen limb. The air/blower valve
      and the exhale valve are made to be normally open so that those paths are unobstructed to allow the patient to
      breathe.
    * **Electrical** To support the air/blower valves and exhale valves being normally open, the Cycle Controller
      watchdog timer is connected to the stepper motor drivers, which will default them to an unpowered state in the
      event of a Cycle Controller computing failure, causing the valves to snap open.

* **Use of stepper motors** - **#TODO** need to fill this out

* **Metric vs imperial** - **#TODO** fill this out when we make a decision

## Valves

* **Pinch Valve (Custom design)**
    * Low cost, robust design for achieving variable flow based on peristaltic tubing.
    * The valve mechanical components are not exposed to the flow, which means it is not exposed to high O2
      concentrations directly.
    * Normally open, which is important for anti-asphyxiation in the case of power loss
    * Still evaluating fatigue and lifetime / sealing.
    * Originally designed as the exhale valve to give control for maintaining PEEP - under considering to use for both
      the air inlet and for the oxygen inlet
    * For more informatin about the design of this valve, see [here](../manufacturing/internals/pinch_valve)

* **Idle Air Control Valve (IAC)**
    * Common automotive part that is cheap and widely available.
    * A linear stepper motor drives a pintle up and down to create a variable orifice.
    * Unclear how these valves perform in high O2 environments or if they could be sufficiently rated/cleaned.
    * Significantly cheaper, more robust, and more widely available than the pinch valve.

* **Proportional Solenoid (PSOL)**
    * Relatively uncommon part but used in traditional ventilators.
    * Provides precise, reliable control of high-pressure gasses.
    * May be cost effective but requires a high-pressure source of oxygen (can not use low pressure sources like oxygen
      concentrators without a booster pump).
    * O2 cleaned PSOLs are relatively hard to find, though are already in use on ventilators. We may be able to clean
      automotive PSOLs.
    * Normally closed, which is important for anti-asphyxiation. **#TODO** need to confirm this

* **One way valve (check valve)**
    * Needs to work in an O2 environment
    * Needs to be reliable and relatively low cost
    * Still figuring out the exact one way valve design
    * Two possibilities are a normal umbrella seat check valve, problem is these have a high cracking pressure. This
      could be OK on the intake side where the fan can generate this but would be a problem on exhale.
    * duckbill valves have also been explored, but these can chatter at low flow rates.
    * Could possibly modify a normal check valve by cutting the spring down or out.

* **Relief Valve**
    * **#TODO** when we figure this out

## Tubing
* Pick peristaltic tubing in the pinch valves so that it can withstand many cycles
* Otherwise any biocompatible tubing is fine, gneerally Tygon for most of the testing.
* Needs to be O2 safe
* 3/4 inch standard allows relatively cheap fittings. Need to transition to metric for int'l.

## Sensors

* **DP sensors / Venturi**
    * The goal of the venturi design is to measure the flow through the system at a limited pressure drop and with a
      large signal.
    * Venturi's are nice because they are cheap and yet can provide reliable flow measurements. See
      [this ticket](https://github.com/RespiraWorks/Ventilator/issues/9) for info about evaluating the venturi's.
    * Currently we are using the difference between the two flow measurements (one for inhale and one for exhale) to
      determine the tidal volume delivered to the patient. We are still evaluating how to do this - see
      [this ticket](https://github.com/RespiraWorks/Ventilator/issues/57) for more information.
    * Another open questions is manufacturing of the venturis - currently the goal is to design a venturi that can be
      injection molded.
    * For more informatni about the venturi design, see [here](../manufacturing/internals/venturi).

* **Patient Pressure sensors**
    * Needs to be reliable, handle many cycles, and meet the required ranges and accuracies of the requirements
      (**#TODO:** flesh this out more).
    * Currently only one sensor is used, but maybe a second one is required for reliability.

* **O2 sensor**
    * The O2 sensor needs to be able to measure up to 100% O2
    * Right now we are using a galvanic cell O2 sensor - but those are known to degrade quickly.
      [This ticket](https://github.com/RespiraWorks/Ventilator/issues/56) is tracking our discussions on this topic.

* **Mass flow sensor***
    * We have shied away from mass flow sensors because they are very expensive when compared to the DP sensor/venturi
      design. However, they are accurate and used on other system so they are not completely ruled out.

## Filters
* Filters on inlet/outlet to prevent contaminents from the surrounding environment getting into the device
* Filter on patient circuit to avoid device contamination and spreading particles between patients
* We're currently looking at HEPA filters since they are commonly avaible and cheap - but we're also evaluating other
  options. HEPA filters are appropriate because they are designed to filter small particles.
  [More info on HEPA filters](https://ntrs.nasa.gov/archive/nasa/casi.ntrs.nasa.gov/20170005166.pdf)
* 2 part mold for holding the filters is meant to be easily manufacturable and to allow easy changing of the filters
  over time
* Filters are placed physically on the outside of the box so they can be replaced without the box being opened

## Blower
* Current blower is not rated to 100% O2, which drives the lack of a blower on the O2 system and a one way valve in
  front of the blower to keep it separate from the high O2 part of the system.
* We have evaluated a large number of blowers. When balancing supply chain, ubiquity of specification, and future
  availability, we settled on this one. However, there is an issue with the pressure spec for the fan. If we needed to
  reach 60 cm H2O, this fan might be under powered. We are currently leaning to not support those high pressures
* **#TODO:** link to the fan we picked

## Enclosure
* Must be sterilizable
* Must be manufacturable with commonly available fabrication equipment in the markets we are assessing (currently
  targeting custom folded sheet metal)
* Enclosed to protect the internals and keep out dust
* Has an external fan for cooling the internal electronics
* Ruggedized and compatible with the hospital environment
* Must support easy assembly and maintenance of the various components

## Humidifier
* Currently planning to use an off the shelf external humidifier—see [this ticket](https://github.com/RespiraWorks/Ventilator/issues/704) for more details.

## PCB/Electronics

* **SRM32 Microcontroller For the Cycle Controller**
    * More powerful than the simpler arduino and Raspberry pis, but still cheap and widely available
    * Used in other medical devices
    * Comes with more powerful/extensive debugging tools
    * Familiar to many of the members of our team
    * See [this ticket](https://github.com/RespiraWorks/Ventilator/issues/709) for more details on why a STM32
      microcontroller was chosen.
* **Rasperry PI and Rasperry PI Touch Screen for GUI**
    * Cheap and widely available
    * Existing libraries for touch screen interactions that can be leveraged
    * Has lower performance requirements than the cycle controller
* **Power Supply**
    * 12V standard chosen to ensure flexibility of power supplies (e.g. battery or UPC)
    * Open question on internal alarms battery
* **#TODO** - need more here.
* **#TODO** - add diagrams from design reviews and such

## Software

* **#TODO** - add diagrams from design reviews and such
### Separation of UI Controller and Cycle Controller
* To maximize safety, it is important to minimize the amount of software that is immediately hazardous to the patient
  (can cause harm in <1s, making human intervention useless), and expose any hazardous software to high levels of
  verification and testing. By moving the UI code to a separate porcess, it reduces risk and saves time because the
  complicated UI code doesn't have to be exposed to the same verification and testing as the cycle controller.

* NOTE: Neither of the controllers are a complete backup for the other - this is not a redundant system.  If either
  fails in a way that is not fixed through the watchdog reset, an immediate intervention will be needed to keep the
  patient alive.  The objective in the case of either failure is to sound the alarm so that the intervention can
  happen - and to design the system such that in the event of a failure there is time to make an intervention.  Making
  a truly redundant system will add cost and time, and so has been deferred for now.

* **Watchdog Timers**
    * In the event of a computing failure in either the UI Computer or the Cycle Controller, a watchdog timer monitors
      each and will reset the offending computer, which should then be able to regain control of the valves.
    * **#TODO** it will need to be confirmed in the final design that the UI Computer cannot command any modes that will
      cause the Cycle Controller to hold these valves closed.

### GUI / UI Controller
* **#TODO** - needs more
* Items that fall within the UI Controller:
    * Cycle Controller Watchdog/Alarm
    * User Parameter Setting
    * Ventilation Mode Setting
    * Sensor Data Reporting
    * Respiratory Cycle Plot Display
    * Alarm Information Display
    * Alarm-specific alert sounds

### Cycle Controller
* **#TODO** - needs more
* Items that fall within the cycle controller:
    * UI Computer Watchdog/Alarm
    * Closed-Loop Valve Control
    * Open-Loop Blower/Valve Control
    * Respiratory cycle Control
    * Sensor Data Reading
    * Sensor Failure Alarm
    * Overpressure Alarm
    * Respiration Rate Alarm
    * Broken Loop Alarm

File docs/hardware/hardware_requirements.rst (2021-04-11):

.. hardware_requirements:

Hardware Requirements Specification
===================================

Purpose
-------

This document describe *what* |PROJECT_NAME| hardware must do.

This document is meant to be read and agreed-upon by the project owners and by software developers during design and construction.

.. todo:: Specify the functional requirements, performance requirements, interface requirements, safety requirements, hazard mitigations

Requirements
------------

Assembly
^^^^^^^^

.. item:: RW-HW-6
   :fulfills: RW-SYS-16

All subcomponents shall pass accelerated life testing equivalent to at least 336 hours (2 weeks continuous runtime)

.. item:: RW-HW-8
   :fulfills:

The construction, assembly, and maintenance of the device shall be compatible with metric tooling/set ups.

.. item:: RW-HW-10
   :fulfills: RW-SYS-16

The device must last 2000 hours if the maintenance schedule is followed.

.. item:: RW-HW-23
   :fulfills:

The ventilator shall be operable by a user wearing standard PPE (e.g. latex or nitrile gloves)

.. item:: RW-HW-30
   :fulfills: RW-SYS-63 RW-SYS-77

The patient circuit shall interface with the vent thru 22mm ID tubing.The patient circuit shall interface with nasal cannulas or pillows through a standard 15mm ET tube adapter interface.

.. item:: RW-HW-33
   :fulfills: RW-SYS-12

The assembly shall feature HEPA filters on the blower intake and exhaust pathways

.. item:: RW-HW-43
   :fulfills: RW-SYS-124

Enclosure openings shall not exceed 12.5mm diameter and shall feature no openings on the top face .

.. item:: RW-HW-44
   :fulfills: RW-SYS-124

Ventilation openings on the enclosure shall not be adjacent to electronics or other sensitive components targeted by IEC 61000-4-1 series of test.

.. item:: RW-HW-45
   :fulfills: RW-SYS-137

All hardware components shall operate without adverse effect at altitudes up to 10000 ft.

.. item:: RW-HW-46
   :fulfills: RW-SYS-140

Enclosure does not degrade when cleaned with X% bleach solution

.. item:: RW-HW-47
   :fulfills: RW-SYS-136

Gas inlet ports are clearly labeled per X

Pneumatics
^^^^^^^^^^

.. item:: RW-HW-3
   :fulfills: RW-SYS-92

The blower shall provide a flow rate of at least 60 L/min.(Stretch goal) the blower shall provide a flow rate of at least 130 L/min.

.. item:: RW-HW-11
   :fulfills: RW-SYS-10

The overpressure relief device shall be set to automatically relieve pressure at or above 60 cm H2O.

.. item:: RW-HW-12
   :fulfills: RW-SYS-144 RW-SYS-92

The device must not let the patient asphyxiate if they are attempting to breathe, even if the device fails. This can be achieved by preventing pressure from dropping below -4 cm H20 and limiting the resistance to 3 cmH20/l/s

.. item:: RW-HW-15
   :fulfills: RW-SYS-42

The pneumatic circuit shall reach maximum flow rate (e.g. 60 L/min) in 100 ms.

.. item:: RW-HW-16
   :fulfills: RW-SYS-89

The device must be able to detect that a patient is trying to trigger an inhale or exhale. This requires being able to measure changes in flow rate to a resolution of 5 L/min during inspiratory and expiratory holds.

.. item:: RW-HW-35
   :fulfills: RW-SYS-76 RW-SYS-24

The oxygen input port shall be DISS compatible up to 440 kPa

Electronics
^^^^^^^^^^^

.. item:: RW-HW-27
   :fulfills: RW-SYS-121 RW-SYS-119 RW-SYS-120

The device shall provide a battery monitor for assessing battery presence, charge, and failure.

.. item:: RW-HW-28
   :fulfills: RW-SYS-121 RW-SYS-120 RW-SYS-119 RW-SYS-117 RW-SYS-118

The device shall provide a sensor indicating whether power is coming from AC or battery and whether AC is available

.. item:: RW-HW-32
   :fulfills: RW-SYS-103 RW-SYS-102 RW-SYS-101 RW-SYS-32 RW-SYS-5 RW-SYS-3

The display shall support touch input, 8-bit color and a minimum refresh rate of 30 fps.

.. item:: RW-HW-34
   :fulfills: RW-SYS-16

The electronic non-volatile memory shall be rated for at least 10e6 read/write cycles.

.. item:: RW-HW-36
   :fulfills: RW-SYS-74 RW-SYS-117 RW-SYS-50

The device battery shall have a charge capacity of X Ah at 12 volts nominal.

.. item:: RW-HW-38
   :fulfills: RW-SYS-69

The electronics shall include a real-time clock with independent battery (e.g. coin cell) supply.

.. item:: RW-HW-39
   :fulfills: RW-SYS-69

The electronics shall include non-volatile memory of at least 1GB

Sensors and Actuators
^^^^^^^^^^^^^^^^^^^^^

.. item:: RW-HW-2
   :fulfills: RW-SYS-111 RW-SYS-110 RW-SYS-115 RW-SYS-3 RW-SYS-5

The pressure sensor shall have a resolution of 1 cmH2O and a range of 0 - 60 cmH2O

.. item:: RW-HW-4
   :fulfills: RW-SYS-113 RW-SYS-112 RW-SYS-116 RW-SYS-115 RW-SYS-89 RW-SYS-32

The inhale and exhale flow sensors shall have a resolution of X L/min and a range of Y L/min.

.. item:: RW-HW-21
   :fulfills: RW-SYS-72

The O2 sensor shall measure oxygen fraction from 21% to 100% with an accuracy of 5%.

.. item:: RW-HW-41
   :fulfills: RW-SYS-122

The temperature sensors shall have range -40 to +125 C with a minimum resolution of 1 C

Traceability Matrix
===================
.. item-matrix:: System Requirements to Hardware Requirements
   :target: RW-SYS-
   :source: RW-HW-
   :sourcetitle: Hardware Requirements
   :targettitle: System Requirements
   :type: fulfills

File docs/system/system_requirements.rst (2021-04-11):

.. system_requirements:

System Requirements
===================

This document defines the system requirements for |PROJECT_NAME|.

Assembly
^^^^^^^^

.. item:: RW-SYS-12
   :fulfills: SR-17

The device shall filter intake and exhaust to below 0.3 um (HEPA) or finer in order to limit the spread of virus from contaminated patients and to prevent the contamination of the device from patients.

.. item:: RW-SYS-16
   :fulfills: SR-28

The device must be able to work continuously (100% duty cycle) for a minimum of 48 hours and a target of 2 weeks without pause for maintenance, downtime, or repair.The device must operate after 2000 hours of storage time.

.. item:: RW-SYS-54
   :fulfills: SR-15

The system components that come into contact with the patient airway circuit shall be compatible with ISO 18562-1 thru ISO 18562-4.

.. item:: RW-SYS-63
   :fulfills: SR-29

The device shall be have the ability to integrate a hot water humidifier, the humidifiers that meet ISO 80601-2-74:2017 are compatible with 22mm Respiratory Tubing per ISO 5356 standard. (Note that the fitting for standard breathing tubes and humidifiers is the same)

.. item:: RW-SYS-124
   :fulfills:

Ventilator shall have ingress protection level of IP21.IP2x = No penetration into ventilator by solid objects > 12.5mm (e.g. fingers)IPx1 = Dripping water (vertically falling drops) shall have no harmful effect.Ref: www.dsmt.com/resources/ip-rating-chart/

.. item:: RW-SYS-136
   :fulfills: SR-34

Gas inlet shall be clearly labelled with gas type, color, and specified pressure ranges along with direction of flow

.. item:: RW-SYS-137
   :fulfills: SR-27

Ventilator shall operate at altitudes below 10k ft

.. item:: RW-SYS-140
   :fulfills: SR-18

The ventilator construction shall continue to operate while being disinfected by standard cleaning agents (e.g. bleach solution of X%)

.. item:: RW-SYS-141
   :fulfills: SR-16

The ventilator design shall include antiviral filters on the patient inhale and exhale limbs.

.. item:: RW-SYS-144
   :fulfills:

Patient shall to be protected against both asphyxiation and barotrauma in the event of a power, mechanical, or computing failure.

.. item:: RW-SYS-150
   :fulfills:

The hardware shall not compromise basic safety and essential performance while stress tested per IEC 60068-2-78 (damp heat).

.. item:: RW-SYS-155
   :fulfills: SR-33

The device, when fully assembled and tested against IEC 60601-1 section 9.6.2, shall not exceed 80 dBa. Test specifications in 80601-2-12 201.9

.. item:: RW-SYS-156
   :fulfills: SR-30

The assembly shall conform to transit-operable (80601-2-12 201.15.3.5.101.2) shock tests per IEC 60068-2-27:5g for 6ms, half-sine, 3x per axis

.. item:: RW-SYS-157
   :fulfills: SR-30

The assembly shall conform to transit-operable (80601-2-12 201.15.3.5.101.2) vibration tests per IEC 60068-2-24. Basic safety and essential performance shall not be compromised during or after this test.10 Hz - 100 Hz: 0.33 (m/s2)2/Hz, 30 min per axis100 Hz - 500 Hz: 6 dB per octave, 30 min per axis

.. item:: RW-SYS-158
   :fulfills: SR-30

The assembly shall conform to transit-operable (80601-2-12 201.15.3.5.101.2) drop tests per IEC 60068-2-31. Basic safety and essential performance shall not be compromised during or after this test.10 cm vertical drop, twice per specified attitude (TBD)NOTE: as of writing it is assumed the ventilator shall weigh between 1-10 kg

Pneumatics
^^^^^^^^^^

.. item:: RW-SYS-9
   :fulfills:

The device shall prevent pressure from dropping below -4 cm H20 and limit the resistance to 3 cmH20/l/s.

.. item:: RW-SYS-10
   :fulfills: SR-20

The device must, through inherently safe features, prevent patient pressures from exceeding 60 cmH2O in any operating cases or failure modes.

.. item:: RW-SYS-24
   :fulfills: SR-12

The device shall be compatible with oxygen (DISS) up to 440 kPa

.. item:: RW-SYS-92
   :fulfills: SR-7

The device shall be capable of a peak inspiratory flow rate of at least 60L/min for at least 30 seconds.NB This supports a minute volume of at least 30 L.

.. item:: RW-SYS-148
   :fulfills:

The pneumatic circuit shall not leak more than 1-2 L/min at 60 cmH2O

Electronics
^^^^^^^^^^^

.. item:: RW-SYS-50
   :fulfills: SR-35

The device battery shall be sized to provide 1 hour of operation at 12 volts nominal.

.. item:: RW-SYS-57
   :fulfills:

The system shall be compatible with 110V/60Hz and 220V/50HZ AC mains.
RW-SYS-069,The ventilator shall provide non-volatile data storage of at least 1GB.,,HW-039

.. item:: RW-SYS-69
   :fulfills:

The ventilator shall provide non-volatile data storage of at least 1GB.

.. item:: RW-SYS-74
   :fulfills:

The ventilator shall be capable of being run from a 12V power supply

.. item:: RW-SYS-149
   :fulfills: SR-24

The device must detect through physical means the disconnection of the oxygen supply from the o2 input line.

.. item:: RW-SYS-153
   :fulfills: SR-33

The 12 volt power supply shall be compatible or certified against IEC 60601-1

.. item:: RW-SYS-154
   :fulfills: SR-22

The hardware shall feature specific sensors for detecting tube dis/connection

.. item:: RW-SYS-159
   :fulfills:

The ventilator shall provide a Real Time Clock for timestamping all event log data

HMI
^^^

.. item:: RW-SYS-3
   :fulfills: SR-26 SR-4

The system shall control the target peak inspiratory pressure (PIP) from 5-55 cmH2O in increments of 1 cm H2O.The system shall measure and numerically display patient pressure in the range of 0 - 60 cmH2O with resolution 1 cmH2O.The system shall display the measured pressure as a graph with duration of 30 seconds updated at a rate >= 20Hz and units of cmH2O.

.. item:: RW-SYS-5
   :fulfills: SR-26 SR-8

The system shall control the target PEEP from 0 - 20 cm H2O in increments of 1 cmH2O.The system shall measure and numerically display the PEEP in the range of 0 - 20 cmH2O in increments of 1 cmH2O.

.. item:: RW-SYS-20
   :fulfills: SR-26 SR-10

The system shall control the respiratory rate (RR) from 5-30 breaths per minute (bpm) in increments of 1 bpm.The system shall measure and numerically display RR in the range of 0 - 30 bpm with resolution 1 bpm.

.. item:: RW-SYS-21
   :fulfills: SR-9

The device shall control the time ratio of inspiration and expiration (I:E ratio) from 1:1 to 1:4 (Inhale to exhale). Increments of 1: 0.1The system shall measure and numerically display I:E ratio in the range of 1:1 to 1:4 with resolution 1:0.1.

.. item:: RW-SYS-32
   :fulfills: SR-26 SR-11

The system shall control inspiratory tidal volumes ranging from 200-800ml with increments of 10mLThe system shall measure and numerically display the inspired tidal volume in range of 0 - 1000 mL with resolution of 10mLThe system shall display the inspired tidal volume as a graph with duration of 30 seconds updated at a rate >= 20Hz and units of mL.

.. item:: RW-SYS-72
   :fulfills: SR-13

The device shall control the fraction of inspired O2 (FiO2) in supplied air from 0.21 to as close to 1 as possible with a minimum of 0.9, adjustable in increments of 0.05.The system shall measure and numerically display the patient FiO2 in range of 21-100% with resolution of 1%.

.. item:: RW-SYS-87
   :fulfills: SR-26

The system shall display the flow rate provided to the patient as a graph with duration of 30 seconds updated at a rate >= 20Hz and units of liters / minute.

.. item:: RW-SYS-143
   :fulfills: SR-11

Ventilator shall support user entry of patient gender and height. This data shall be used to calculate ideal body weight (IBW).Ventilator shall support the display of tidal volumes as both volume (units mL) and volume per kg IBW (units mL/kg or cc/kg)

.. item:: RW-SYS-147
   :fulfills:

The system shall display pressure/volume loops.

Manager
^^^^^^^

.. item:: RW-SYS-77
   :fulfills:

The system shall support a HFNC operational mode. In this mode there are no breath cycles. The operator defines the following control parameters:constant flow rate (up to maximum possible L/min)constant FiO2 (21-100%).Display parameters: Patient pressure (cmH2O), flow rate (L/min), FiO2 %Relevant alarms: Low/high FiO2 triggers, Low/high pressures

.. item:: RW-SYS-131
   :fulfills:

The ventilator shall have a pre-test mode where the patient inhalation port and patient exhalation port are connected and the operation of the device is checked including the capability to produce the correct pressure and flow rate, the function of valves, and the function of tidal volume measurement.

.. item:: RW-SYS-132
   :fulfills: SR-6 SR-4 SR-2 SR-1

The system shall support Pressure Assist Mode. In this mode a breath cycle is defined by the control parameters below. The patient can exceed the respiratory rate by initiating additional breaths, but the breath parameters do not change.Control parameters:PIP. Peak Inspiratory Pressure.PEEP. Positive End-Exhalatory Pressure.FiO2. Fraction of Inspired Oxygen.I-time. Inspiratory (rise + dwell) time.Inspiratory sensitivity.RR. Respiratory Rate.Display parameters: PIP/PEEP/RR/FiO2/I:E ratio/tidal volume.Relevant Alarms: * Low tidal volume * High tidal volume * High RR

.. item:: RW-SYS-133
   :fulfills: SR-5

The system shall support Pressure Support Mode. In this mode the breath cycle shall be defined by the control parameters below. The breath cycle shall be triggered exclusively by the patient.Control parameters:SIP: Support Inspiratory Pressure. Like PIP, but specified as a support pressure, not a target pressure.PEEP. Positive End-Exhalatory Pressure.FiO2. Fraction of Inspired Oxygen.I-time. Inspiratory (rise + dwell) time.Inspiratory sensitivity (change in flow rate at PEEP)Expiratory sensitivity (change in flow rate at P_plateau)Display parameters: PIP/PEEP/RR/FiO2/I:E ratio/tidal volume.Relevant Alarms: * Low tidal volume * High tidal volume * Low RR (apnea) *

.. item:: RW-SYS-134
   :fulfills:

The system shall support Pressure Control Mode. This mode shall not be featured. It is effectively a subset of Pressure Assist with zero patient inspiratory effort.

.. item:: RW-SYS-146
   :fulfills: SR-3

The system shall support Volume Assist mode. In this mode a breath cycle is defined by the control parameters below. The patient can exceed the respiratory rate by initiating additional breaths, but the breath parameters do not change.Control parameters:VT. Tidal volume.PEEP. Positive End-Exhalatory Pressure.FiO2. Fraction of Inspired Oxygen.I-time. Inspiratory (rise + dwell) time.Inspiratory sensitivity.Expiratory sensitivity.RR. Respiratory Rate.Display parameters: PIP/PEEP/RR/FiO2/I:E ratio/tidal volume.Relevant Alarms: * Low pressure * High pressure * High RR

.. item:: RW-SYS-160
   :fulfills:

The manager shall log at least 5000 events in an event log, including at least the following items:- Ventilation starts and stops- All confirmed Ventilation settings- All confirmed alarm settings- All occurrences and ends of alarms with all their related actions: Inhibitions, cancellations, resets, acknowledge button presses.

.. item:: RW-SYS-161
   :fulfills: SR-11

Measurement of tidal volume must be accurate to within 10mL

.. item:: RW-SYS-163
   :fulfills: SR-20

GUI must compute PIP over each breath

.. item:: RW-SYS-164
   :fulfills: SR-10

GUI must compute the breath rate based on controller sensor readings

.. item:: RW-SYS-165
   :fulfills: SR-9

Algs must be able to detect inspiration and expiration phase and how long it took.

.. item:: RW-SYS-167
   :fulfills: SR-30

GUI needs to automatically invoke a safety action when blower motor temperature is above threshold

.. item:: RW-SYS-168
   :fulfills:

GUI should be able to compute the rise time for each breath

.. item:: RW-SYS-169
   :fulfills:

Controller must keep track of #cycles of wear of various components and issue alarms if they're nearing their lifespan

Controller
^^^^^^^^^^

.. item:: RW-SYS-42
   :fulfills:

The device shall reach the commanded patient pressure within 100 ms of detecting respiratory effort.

.. item:: RW-SYS-89
   :fulfills: SR-5

The minimum detectable inspiratory effort shall be 5 L/min.

.. item:: RW-SYS-94
   :fulfills: SR-20

The pressure overshoot during the pressure fall phase shall not exceed 0.8*PEEP-1 cmH2O

.. item:: RW-SYS-95
   :fulfills: SR-20

The pressure overshoot during the pressure rise phase shall not exceed 2 cmH2O.

.. item:: RW-SYS-142
   :fulfills: SR-31

The device shall ensure control parameters are within 10% of commanded values in each of the test conditions specified in 80601-2-12 table 201.104.

.. item:: RW-SYS-152
   :fulfills:

The device needs to be able to achieve the FiO2 target within 30-60s

.. item:: RW-SYS-162
   :fulfills:

Controller must detect onset of respiratory effort within X ms

.. item:: RW-SYS-166
   :fulfills:

Controller shall report to the Manager the moments when each breath begins (patient-triggered or automatic)

Alarms
^^^^^^

.. item:: RW-SYS-17
   :fulfills: SR-25

The device parameters and alarms shall be readable at a distance of 1 meter.The device alarms shall be audible (60-80 dBa) at a distance of 1m

.. item:: RW-SYS-68
   :fulfills:

The device shall be allow the user to view all alarms if multiple alarms are simultaneously present.

.. item:: RW-SYS-98
   :fulfills:

The system shall have multiple priority alarms indicating the severity of the condition. These modes shall be:High - Likely to cause PATIENT injury or death within seconds to several minutes if uncorrectedMedium - Do not cause PATIENT injury or death until at least several to many minutes have elapsedLow - May cause PATIENT injury only after many minutes to hours have passed

.. item:: RW-SYS-101
   :fulfills:

High severity visual alarms shall be indicated with a red color and a flashing frequency of 1.4-2.8 Hz with a 20-60% duty cycle.High severity audio alarms shall have the following characteristics defined by 60601-1-8:an auditory burst of 10 pulsespulse tone frequency shall be 150-1000Hz.There shall be at least 4 harmonic components of the pulse tone in the range 300-4000 Hz.The effective pulse duration shall be 75-200 ms.See attached table for burst description.

.. item:: RW-SYS-102
   :fulfills:

Low severity alarms shall be indicated with a cyan or yellow color which shall be constantly on.

.. item:: RW-SYS-103
   :fulfills:

Medium severity alarms shall be visually indicated with a yellow color, and a flashing frequency of 0.4-0.8Hz with a 20-60% duty cycleMedium severity alarms shall have the following characteristics defined by 60601-1-8:pulse tone frequency shall be 150-1000Hz.There shall be at least 4 harmonic components of the pulse tone in the range 300-4000 Hz.The effective pulse duration shall be 125-250 ms.See attached table for burst description.

.. item:: RW-SYS-106
   :fulfills:

A press on the AUDIO PAUSE / ALARM PAUSE key shall initiate an auditory alarm signal pause of all active alarms up to 120 seconds. The alarm activation symbol shall be displayed during the inactivation state with the symbol IEC 60417-5576

.. item:: RW-SYS-107
   :fulfills:

The system shall have a means to dismiss alarms which have been previously triggered.

.. item:: RW-SYS-110
   :fulfills: SR-22

The operator can set a threshold for a low patient pressure alarm in the following ranges:Low Patient Pressure alarm: 0-20 cmH2O, 1 cmH2O incrementsWhen the alarm thresholds are triggered the system shall initiate a high priority alarm.

.. item:: RW-SYS-111
   :fulfills: SR-20

The operator can set a threshold for a high patient pressure alarm in the following ranges:High Patient Pressure alarm: 20-60 cmH2O, 1 cmH2O increments. Default: PIP+5 cmH2OThis alarm shall trigger if the patient pressure exceeds the set PIP for three consecutive breath cycles.The audible indicator shall silence upon the first breath that goes below the threshold, but the visual indicator shall remain active until the alarm is cleared.

.. item:: RW-SYS-112
   :fulfills: SR-23

The operator can set thresholds for low and high exhaled tidal volume (VTE) alarms in the following ranges:High VTE alarm: 500-3000 mL, 10 mL incrementsLow VTE alarm: 0-1000 mL, 10 mL incrementsWhen the alarm thresholds are triggered the system shall initiate a medium priority alarm.This alarm does not apply in HFNC mode.

.. item:: RW-SYS-113
   :fulfills: SR-23

The operator can set thresholds for low and high inspired tidal volume (VTI) alarms in the following ranges:High VTI alarm: 500-3000 mL, 10 mL incrementsLow VTI alarm: 0-1000 mL, 10 mL incrementsWhen the alarm thresholds are triggered the system shall initiate a medium priority alarm.This alarm does not apply in HFNC mode.

.. item:: RW-SYS-114
   :fulfills: SR-22

The ventilator shall initiate a high priority alarm when the proximal tube is not connected for all ventilation modes.

.. item:: RW-SYS-115
   :fulfills: SR-23

The ventilator shall initiate a high priority alarm if no significant volume can be delivered to the patient while the target pressure is reached (e.g. patient circuit blockage detected).

.. item:: RW-SYS-116
   :fulfills:

The operator can set a maximum leak threshold as follows:* Leak threshold: 5-60 L/min, 1 L/min incrementsA high priority alarm shall be triggered when leakage above this threshold is observed in the patient circuit.

.. item:: RW-SYS-117
   :fulfills:

The ventilator shall initiate continuous tone alarm when shut down occurs while ventilating. The alarm shall last at least 2 min.

.. item:: RW-SYS-118
   :fulfills: SR-19

The ventilator shall provide a low priority alarm if an AC power source (previously available) is lost or disconnected

.. item:: RW-SYS-119
   :fulfills: SR-19

A ventilator operating on battery shall provide a medium priority alarm when the estimated remaining operating time is 30 minutes or below.

.. item:: RW-SYS-120
   :fulfills: SR-19

A ventilator operating on battery shall provide a high priority alarm when the estimated remaining operating time is 10 minutes or below.

.. item:: RW-SYS-121
   :fulfills:

The ventilator shall provide a high priority alarm if the battery is absent or not available, or if the battery is unchargeable.

.. item:: RW-SYS-122
   :fulfills:

Temperatures of critical system elements shall be monitored. A high priority alarm shall trigger if these elements exceed their recommended temperatures.BlowerElectronicsBatteryTBD: Do we cut back on ventilation as a fallback (preserve the ventilator at risk to patient)

.. item:: RW-SYS-128
   :fulfills: SR-6 SR-21

The operator can set thresholds for low and high respiratory rate (RR) alarms in the following ranges:High RR alarm: 5-30 bpm, 1 bpm incrementsLow RR alarm: 2-30 bpm, 1 bpm incrementsWhen the alarm thresholds are triggered the system shall initiate a medium priority alarm.This alarm does not apply in HFNC mode.

.. item:: RW-SYS-139
   :fulfills: SR-24

The ventilator shall issue a high priority alarm in the event of O2 disconnection

.. item:: RW-SYS-151
   :fulfills: SR-25

The device shall provide an audible alarm system that can:provide volume at 60 dBa from 150 Hz to 4000 Hzproduce volume from an electrical signal within 33 ms

Traceability Matrix
===================
.. item-matrix:: System Requirements to SRS
   :source: RW-SYS
   :target: RW-SW
   :targettitle: Software Requirements
   :sourcetitle: System Requirements
   :type: fulfilled_by

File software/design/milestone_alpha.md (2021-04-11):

# This milestone is complete.

_Information below only for posterity._

# Objectives
* Provide a physical proof-of-concept for demonstration and review with medical experts
  * See **Demo script** section below.

* Provide a platform for continuous engineering experimentation
  * E.g. Edwin will want to play with the thing with a test lung. Ideally the software should be conductive to that, e.g. have the parameters adjustable via UI rather than baked in.

# Requirements

* Must have a minimal GUI (graphical user interface) that can display pressure trace, flow trace, volume trace
  * GUI is ideally our specialized QT GUI, but if that's not ready by demo time, we can use [DEPRECATED LINK].
    * *jlebar*: That approach won't work with our current protobuf-based protocol.  We can change our code to output something parseable by that tool if necessary, but my preference would be to do something that we don't have to throw away.  For example, Albertas put together a [proof of concept Python script](https://github.com/RespiraWorks/Ventilator/commit/330895ea391ee70cf156fb5bd8673434b3908846) that reads protobuf data from the Arduino.  We could use an approach like this to draw graphs in Python.

* GUI must obtain pressure, flow, volume data from the controller
  * [Per Ethan](https://respiraworks.slack.com/archives/C012H3G1GQ5/p1587857837002500): Flow/volume do not need to be right, just look right:
  * Ideally, use sensor readings with calibration at device startup and smoothing
  * But for alpha, OK to do calibration once on the demo device and hard-code calibration parameters; omit smoothing
  * Absolute worst case, use synthetic data for demo

* Controller must implement Pressure Control (aka Command Pressure) mode
  * Defined in [this presentation slide](https://docs.google.com/presentation/d/1DA1BQlCj8wNv60pGGzrldPfZBmr6WAH4WbrD4W7i43U/edit#slide=id.g739b1a32cc_0_12), prototyped in [pid.cpp](https://github.com/RespiraWorks/Ventilator/blob/fee155d5d4e8fa029b2e83e4753cfaeb15b9b365/controller/src/pid.cpp), correct implementation tracked [here](https://github.com/RespiraWorks/Ventilator/issues/17)
  * Within alpha, for demo, controller can implement this autonomously, i.e. with parameters hard-coded in the controller rather than obtained from the GUI.
  * However, getting mode parameters from GUI is a nice-to-have, per objective 2 above.

* Must not crash irrecoverably or self-destruct.

# Demo Script
This is a narrative description of how we expect the alpha test to go.  We will probably be running a subset of the tests described in Appendix B of the [MHRA Requirements](https://assets.publishing.service.gov.uk/government/uploads/system/uploads/attachment_data/file/879382/RMVS001_v4.pdf).

* Hook up RespiraWorks Ventilator to a test lung
* Turn on device and begin showing data on a screen, either on the GUI or a laptop
* Run a set of respiratory cycles at default, middle of the range values.
* Adjust each of PIP, PEEP, I:E, and RR one at a time, starting from default values, while recording data.
* Run some of the more extreme corner cases involving two or more of the above settings (i.e. High PIP, low PEEP, Low I:E, high RR, high resistance on test lung, high compliance on test lung), while recording data.
* Simulate common failure modes (leaky loop, patient obstruction, etc), while recording data.
* Simulate patient inspiratory effort, record data.
* End test

*TODO(2020-04-29)* Clarify with Edwin: What behavior do we expect SW to have in extreme cases / failure modes?  Similarly, what behavior do we expect when simulating patient effort?  Current understanding is that, nothing is needed from software.

* Note: For patient effort, failure modes, and corner cases, we don't except the alpha software to do anything except continue to drive the respiration cycle according to the set parameters.  We just want to record what these cases look like to our sensors.

# Excluded

The alpha milestone is part of the project's overall [requirements](https://respiraworks.github.io/Ventilator/software/SRS.html). Anything mentioned there but not here, is excluded from alpha.

If you have further questions, ask on [#alpha-reqs](https://app.slack.com/client/T0102KRCH5M/C012H3G1GQ5/thread/C0100SF3N5T-1587858521.093800).

# Issue hotlists

Proceed with caution: these need cleanup.

- Controller: https://github.com/RespiraWorks/Ventilator/milestone/4
- GUI: https://github.com/RespiraWorks/Ventilator/milestone/1

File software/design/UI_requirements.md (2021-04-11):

# User Interface Requirements

The UI runs on a 1024x600 touchscreen. There are no external buttons or anything.

The UI requirements below come from several sources:
* Original mock-ups (the black-and-white mockups included
  [here](https://www.ics.com/blog/ics-joins-respiraworks-on-ventilator-project))
* [ICS prototype](http://demo.ics.com/ventilatorui-demo/) that was built based on the mock-ups
* [This paper](https://ccforum.biomedcentral.com/articles/10.1186/s13054-016-1431-1) and
  [this demo](https://www.youtube.com/watch?v=BT3snJ1Hm2s)
* [These notes](https://docs.google.com/document/d/1QFFcg2gL3PXXzyqgSBz3XZQm_oobZ2osFuErh492UEA/edit) from a
  conversation with a respiratory therapist

The list below is incomplete and possibly wrong in some ways.
Please consult SRS [Requirements page](https://respiraworks.github.io/Ventilator/software/SRS.html).
However, Valispace also does not have complete information at the time of writing. Proceed with caution.

## Self-test mode

On startup, ventilator is in self-test mode. It performs a set of checks and reports on the status.

Some checks are **automatic** _(eg that a certain tube is not blocked: turn on the blower, check that output flow
sensor detects some flow)_, Some are **manual** _(eg for "the buzzer works" it needs to turn on the buzzer and ask user
whether it's audible)_

The **full set of checks** is not yet known and generally open-ended.
Checks should include **guidance on how to fix** if it failed.
The self-test mode should be easy to use _(the hospital where the therapist above works decided not to purchase vents
where it was too cumbersome)_.
Results of self-test should be retained in memory.

**Open questions:**
* Should you be able to perform self-test only on startup or at any time?
* Should you confirm that patient is not connected?
* Should device refuse to operate if a check fails?

See also https://github.com/RespiraWorks/Ventilator/issues/307.

## Ventilation modes

We intend to support **Command Pressure** _(device commands all breaths)_, **Pressure Assist** _(device detects inhale
effort and helps that breath, but also initiates breaths if patient doesn't)_, **CPAP with O2 therapy aka HFNC** _(light
constant positive O2-saturated air pressure, non-invasive)_.

_Note: Different sources seem to indicate that pressure-controlled modes are going out of favor and volume control is
preferable (regular - not PRVC or VC+) - eg see
[notes](https://docs.google.com/document/d/1QFFcg2gL3PXXzyqgSBz3XZQm_oobZ2osFuErh492UEA/edit). But for v0.2 we're doing
pressure control._

**Mode parameters**: Each mode has several parameters defining it, e.g. Respiratory Rate, PIP (Peak Inspiratory
Pressure), PEEP (Positive End-Expiratory Pressure), FiO2 (O2 percentage). Parameter changes must be confirmed before
taking effect.

**Displayed measurements**: In each mode we display real-time graphs and sensor readings of several measured values:
pressure, flow, volume.

**Measured vs. commanded values**: All or almost all values have a "commanded" and "measured" value. E.g. ventilator
tries to achieve a certain PIP - this is the "commanded" value - but what it actually achieves is the "measured" value.
If they're too far off, this is bad and usually triggers an alarm.
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

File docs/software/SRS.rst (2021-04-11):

.. SRS:

Software Requirements Specification
===================================

Purpose
-------

This document describe *what* |PROJECT_NAME| software must do.

This document is meant to be read and agreed-upon by the project owners and by software developers during design and construction.

.. todo:: Specify the functional requirements, performance requirements, interface requirements, safety requirements, hazard mitigations

Requirements
------------

General
^^^^^^^

.. item:: RW-SW-8
   :fulfills: RW-SYS-16

All software clocks must have high enough range to not overflow within 2 weeks

.. item:: RW-SW-9
   :fulfills: RW-SYS-16

Numeric algorithms within the software must not lose stability over 2 weeks

.. item:: RW-SW-10
   :fulfills: RW-SYS-16

Software algorithms must be runnable in faster than real time to allow stress testing of long-term continuous operation

.. item:: RW-SW-18
   :fulfills: RW-SYS-50

Software (both controller and Pi) should be power-efficient enough to continuously work from battery for 1 hour

.. item:: RW-SW-154
   :fulfills: RW-SYS-132

Controller must be able to detect patient inspiration

Alarms
^^^^^^

.. item:: RW-SW-1
   :fulfills:

GUI must have an alarm that triggers when the input air line is blocked (leading to low pressure), with severity HIGH

.. item:: RW-SW-2
   :fulfills:

GUI must have an alarm that triggers when the input O2 line is blocked (leading to low pressure), with severity HIGH

.. item:: RW-SW-3
   :fulfills: RW-SYS-9

Device and GUI must have an alarm for inspiratory pressure dropping below -4cm H2O

.. item:: RW-SW-3
   :fulfills:
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

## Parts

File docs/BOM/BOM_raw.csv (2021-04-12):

Item | Quantity | Manufacturer | Part # | Price (USD) | Sources | Notes
A1 | 1 | RespiraWorks | upper_acrylic_face_panel |  | Rw | Upper acrylic face panel
A2 | 1 | McMaster-Carr | 7768K22 | 11.62 | C | brass threaded check valve, DUPLICATE in pneumatic assembly
A3 | 1 | McMaster-Carr | 50785K273 | 8.23 | C | through-wall straight connector, 1/4NPT female, DUPLICATE in pneumatic assembly
A4 | 1 | McMaster-Carr | 5121K451 | 5.78 / 10 | C | 1/4 NPT x 1/4" ID barbed adapter, DUPLICATE in pneumatic assembly
A5 | 1 | UPerfect | - | 49 | C | 7" capacitive touchscreen, DUPLICATE in electrical assembly

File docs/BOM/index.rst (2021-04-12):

.. _BOM_index:

BOM
======================

.. csv-table:: BOM
   :file: BOM_formatted.csv
   :widths: 30, 30, 30, 10
   :header-rows: 1

.. toctree::
   :maxdepth: 2

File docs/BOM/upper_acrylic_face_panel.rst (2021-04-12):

.. _upper_acrylic_face_panel:

Upper Acrylic Face Panel
========================

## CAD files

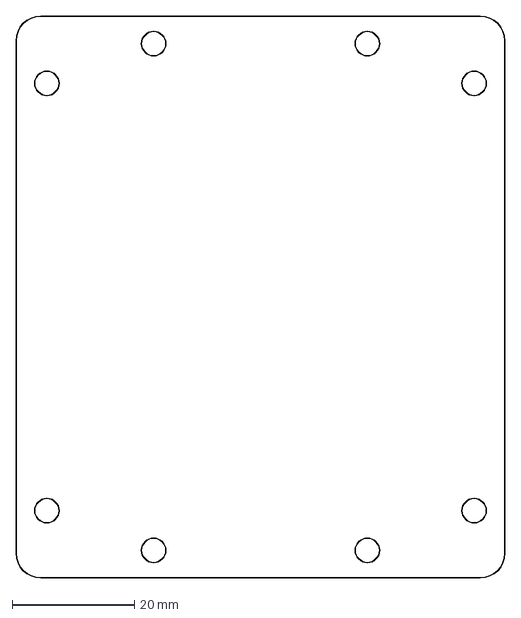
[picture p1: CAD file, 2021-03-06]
manufacturing/internals/blower/exports/driver_mounting_plate.dxf
80.0 x 92.0 mm

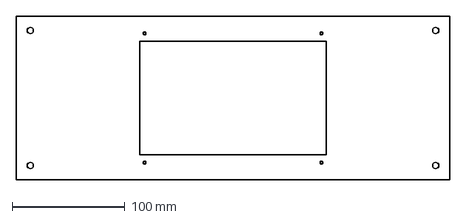
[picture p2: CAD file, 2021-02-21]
manufacturing/internals/display_panel/exports/display_panel_acrylic_plate.dxf
385.0 x 145.0 mm

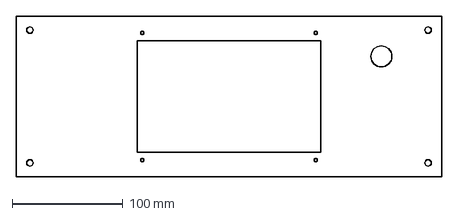
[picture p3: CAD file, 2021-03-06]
manufacturing/internals/filter_panel/exports/filter_panel_acrylic_plate.dxf
385.0 x 145.0 mm

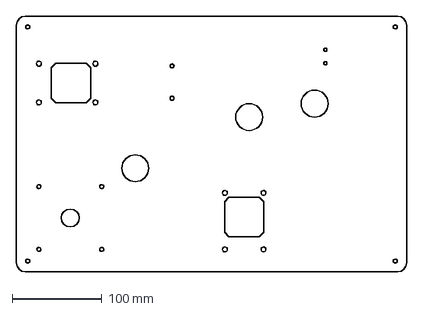
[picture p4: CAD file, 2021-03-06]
manufacturing/internals/tray/exports/pneumatics_tray.dxf
435.0 x 285.0 mm

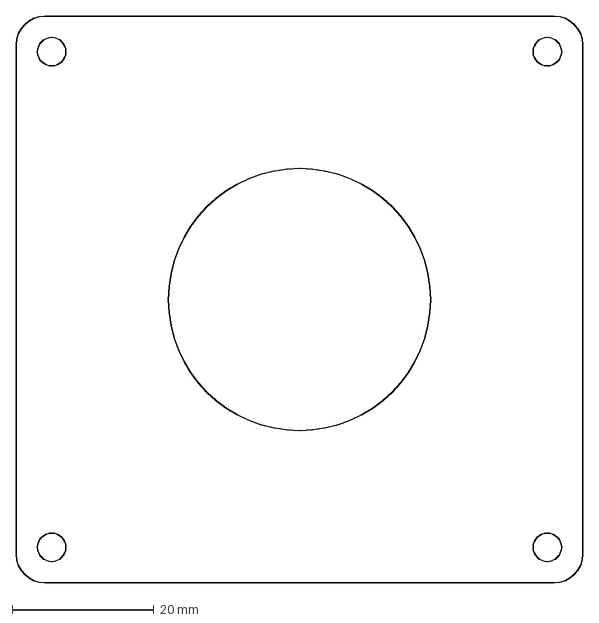
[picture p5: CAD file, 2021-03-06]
manufacturing/internals/blower/exports/tubing_adapter_holding_plate.dxf
80.0 x 80.0 mm

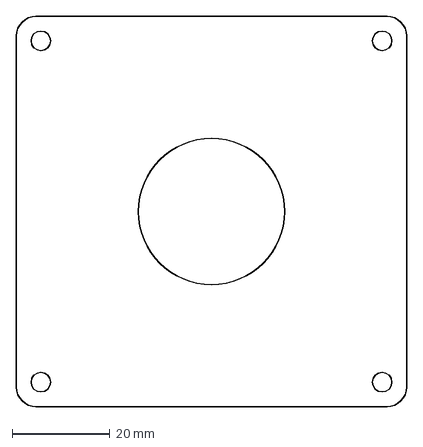
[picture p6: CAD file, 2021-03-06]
manufacturing/internals/blower/exports/blower_holding_plate.dxf
80.0 x 80.0 mm

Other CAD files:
manufacturing/internals/filter_panel/filter_holder/exports/filter_cover_air_vent.stl
manufacturing/internals/manifold/oxygen_relief_manifold.stl
manufacturing/internals/mixer/oxygen_mixer.stl
manufacturing/internals/pinch_valve/exports/pinch_valve_base.stl
manufacturing/internals/reducer_3-4_1-4/tubing_reducer_1-4in_x_3-4in.stl
manufacturing/internals/venturi/exports/venturi_exhale.stl
manufacturing/internals/filter_panel/filter_holder/exports/filter_cover_patient_connector.stl
manufacturing/internals/pinch_valve/exports/pinch_valve_rotor.stl
manufacturing/internals/venturi/exports/venturi_generic.stl
manufacturing/internals/filter_panel/filter_holder/exports/filter_housing.stl
manufacturing/internals/venturi/exports/venturi_air_influx.stl
manufacturing/internals/blower/exports/tubing_adapter.stl
manufacturing/closure_panel/closure_assembly.iam
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

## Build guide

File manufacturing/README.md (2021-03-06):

# Manufacturing design

| Full assembly rendering    |  Internals   |
|:---:|:---:|
|  |  |

This section of the repository describes the physical design of the ventilator and the process of manufacturing the
components and fully assembled units.

## DISCLAIMERS

**This is an incomplete, as yet untested design that is not yet intended to be used on patients.**

**The repository contains live documents. All documentation here is on a "best effort" but no guarantee basis.
Information is incomplete. Pictures, renderings, parts lists and fabrication instructions may contradict each other.
Components may or may not connect and integrate as intended. Contents may also be out of date. If you
decide to buy or build anything, do so at your own risk.**

**FIRE HAZARD** The below design is not fundamentally safe to be used or tested with oxygen or other volatile gases.
Parts of the pneumatic design address the need for controlled pressurized oxygen supply. These aspects of the design
have only been tested with pressurized air as proof of concept. Listed components are not safe to use with
concentrated oxygen. Oxygen is a volatile substance and at high concentration is an extreme fire hazard. Do not
do anything stupid.

**No endorsements.** Materials listed in these pages include links to various suppliers. This does not constitute
any endorsement of specific products nor indication that those components are appropriate and reliable for use in
medical devices. These links are simply here for our own convenience, since we all use the repository as our common
collaboration space.

**Acknowledgements:** The following pages contain CAD models for various off-the-shelf components, such as valves,
fittings and screws. These have been provided by various suppliers on their websites and may be intellectual
property of the respective manufacturer. These models come with no guarantees and do **NOT** fall under the
[Apache license](../LICENSE) which generally applies the rest of our project.

## Contributing

If you are a pneumatics or mechanical engineer and intend to contribute to our design, please read
our [wiki](https://github.com/RespiraWorks/Ventilator/wiki), by which we mean **all of it**.

If you intend to make any physical components yourself, please become familiar with the
[manufacturing methods guide](methods). And please help maintain it.

## Design principles

### Logical structure

The following pages and CAD models are structured according to the sub-assembly hierarchy that should be followed
in building the ventilator. In general, each subassembly CAD model resides in its own directory and should be
accompanied by a README file, any renderings, drawings or photos of the physical implementation, exported
files for 3d printing or whatever other manufacturing process. The readme file is there to explain the design rationale
and any non-trivial manufacturing or quality control steps necessary to produce the part.

There are directories for each custom-designed component or custom assembly involving off-the-shelf components
arranged in a special way, or some mix thereof. Off-the-shelf CAD models all reside in the [third_party](third_party)
directory with some categorization. If a component requires custom manufacturing, you can safely assume that the
necessary files will be in its own directory.

This is a on a best effort basis, so some hardware may reside with CAD assemblies of a scope higher or lower from where
they are listed in the parts tables. You should always consult both CAD and verbal documentation before attempting to
build anything. It is highly advised that you have your parts and measure them to confirm expected dimensions match,
as models may be imprecise.

### Metal frame and enclosure

The current version of the ventilator assembly is meant to demonstrate its packaging in "production" housing. Based
on lessons learned from previous iterations, the ventilator uses a detachable internal assembly, to which all pneumatic
components can be mounted and connected. This allows for 360 degree accessibility to components during initial
assembly. When complete, this internal assembly is bolted into the enclosure, and the enclosure is screwed shut. The
top-rear positioning of the removable enclosure lid provides access to components that will need routine maintenance.

We chose a sheet metal construction because:
* it is cheap and quick - sheet metal is cheap to fabricate. Unlike plastic parts, it doesn't require any expensive
  molds. This is great for prototyping stages and should also be an accessible manufacture process in many countries.
* strength and durability - stainless steel and other highly durable materials can be used. The frame and enclosure
  should be rigid and withstand mechanical stresses. The simple two-piece enclosure should prove to be quite rugged.
* staged assembly - we wanted the ability to assemble all internals outside the enclosure. The design is built around
  a strong bracket upon which all pneumatics and electrical equipment is installed. This makes assembly and maintenance
  easier. Also useful when prototyping and making design modifications.

### Choice of hardware

* **metric** - preference has been given to metric hardware. Metric standard hardware is available worldwide, including
  countries that prefer imperial standard, but generally not vice versa.
* **hex drive** - screws with hex drive interface have been chosen. Phillips drive screws are prone to cam-out. Torx
  and other interfaces may be too exotic and supply chains may be limited in some parts of the world. Hex drive is
  practical and ubiquitous enough.
* **button head** - preference is given to button head screws. These are smaller and more flush with the surface than
  pan head or socket head screws and thus less likely to catch on clothing or other materials, and are also the least
  visually obtrusive.
* **predominantly M4** - where possible, we are standardizing to M4 mounting components. This is to minimize the variety
  of components to keep in inventory.

## Parts

If you are a member of the team and intend to build your own prototype, please read the
[purchasing guidelines](purchasing_guidelines.md) first.

[ppg]: purchasing_guidelines.md

| Item  | Quantity | Manufacturer  | Part #                       | Price (USD) | Sources[*][ppg]| Notes |
| ----- |---------:| ------------- | ---------------------------- | -----------:|:--------------:|:------|
|**A1** | 1        | RespiraWorks  | [Wiring harnesses][a1rw]     | (0.0)       | Rw             | Wiring harnesses: these get integrated into the below assemblies |
|**A2** | 1        | RespiraWorks  | [Internals][a2rw]            | 1327.82     | Rw             | Internals assembly - includes most pneumatics, electrical and computing components |
|**A3** | 1        | RespiraWorks  | [Enclosure][a3rw]            | 430.90      | Rw             | Metal enclosure that contains and protects the ventilator internals |
|**A4** | 1        | RespiraWorks  | [Cooling fan assembly][a4rw] | 29.69       | Rw             | For removing heat generated by electrical equipment |
|**A5** | 1        | RespiraWorks  | [Closure panel][a5rw]        | 119.01      | Rw             | Completes the enclosure and provides power input interface |
|**A6** | 12       | McMaster-Carr | 92095A188                    | 0.10        | [C][a6mcmc]    | M4 screws, 6mm: main bracket and closure fastening |
|**A7** | 1        | RespiraWorks  | [Peripherals][a7rw]          | 72.98       | Rw             | Indispensable components that are strictly outside of the assembly itself |

**Total price estimate:** USD 1981.60

[a1rw]:   wiring
[a2rw]:   internals
[a3rw]:   enclosure
[a4rw]:   cooling_fan
[a5rw]:   closure_panel
[a6mcmc]: https://www.mcmaster.com/92095A188/
[a7rw]:   peripherals.md

## General assembly

Ventilator full assembly CAD model: [.iam](ventilator_assembly.iam)

>**TODO:** drawings

### Pre-fabrication

A number of custom components may have to be pre-fabricated by contract manufacturer:

* Main board / PCB and daughter board (in [electronics assembly](internals/display_panel/electronics))
* Sheet metal components: [equipment bracket](internals/tray), [enclosure](enclosure) and [closure panel](closure_panel)
* Acrylic components: [pneumatics tray](internals/tray), [display panel](internals/display_panel) and
  [filter panel](internals/filter_panel).

There are also various 3d printed components throughout the sub-assemblies. They will not be listed here explicitly.
Familiarize yourself with the entire hierarchy of assemblies and print what is needed ahead of time.

### Order of assembly:

* Prepare all custom wiring components `[A1]`
* Complete the internals assembly with all its sub-assemblies `[A2]`
* Insert internals assembly into enclosure `[A3]` and fasten it to the sides with 6x M4 screws `[A6]`
* Install cooling fan `[A4]` (optional)
* Attach main power harness to the PCB and install the closure panel `[A5]` using the remaining screws `[A6]`
* Attach power cables and/or human input devices listed in [peripherals page](peripherals.md)

Once the assembly is complete, you may proceed to the [software](../software) section of the repository
and learn how to get its brain working.

## Additional notes

While this page is not comprehensive yet, some aspects of connecting sensor tubing and electronics may still be
better covered in the (somewhat obsolete) "pizza build" [guide](../quality-assurance/testing/pizza_build).

Some aspects of the production packaged design are detailed in the first section of the (somewhat obsolete)
[assembly video](https://youtu.be/2hdV5CWcLb4).

## Living prototypes

There are currently at least 3 prototypes being worked on in various locations around the world:

|     |     |     |
|:---:|:---:|:---:|
| Germantown Maryland  |  |  |
| Sunnyvale California |  |  |
| Visakhapatnam India  |  |  |

### Test equipment

To test a prototype you will need some additional components that are not strictly part of the ventilator itself, such
as test lungs. There is additional information on the [testing](../quality-assurance/testing) page under the quality
assurance section of the repository.

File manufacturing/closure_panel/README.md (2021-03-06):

# Closure panel

| Rendering | Assembled |
|:-------------------------:|:-------------------------:|
|  |  |

## Design rationale

> **TODO:** Content..

## Parts

**Note: If you are a member of the RespiraWorks team, review the [part purchasing guidelines][ppg]
BEFORE purchasing any parts.**

[ppg]: ../purchasing_guidelines.md

| Item  | Quantity | Manufacturer  | Part #                     | Price (USD) | Sources[*][ppg]| Notes |
| ----- |---------:| ------------- | -------------------------- | -----------:|:--------------:|:------|
|**A1** | 1        | RespiraWorks  | [Closure panel][a1rw]      | 109.25      | Rw             | Ventilator closure (back panel), bent sheet metal |
|**A2** | 1        | RespiraWorks  | [Main power harness][a2rw] | 8.61        | Rw             | Main power wire harness, with 4pin DIN female plug |
|**A3** | 2        | McMaster-Carr | 92095A461                  | 0.38        | [C][a3mcmc]    | M2.5 screw, 12mm |
|**A4** | 2        | McMaster-Carr | 93625A102                  | 0.11        | [C][a4mcmc]    | M2.5 locknut |
|**A5** | 1        | McMaster-Carr | 92095A189                  | 0.09        | [C][a5mcmc]    | M4 screw, 8mm |
|**A6** | 1        | McMaster-Carr | 93475A230                  | 0.02        | [C][a6mcmc]    | M4 washer, 9mm OD |
|**A7** | 1        | McMaster-Carr | 93625A150                  | 0.06        | [C][a7mcmc]    | M4 locknut |

**Total assembly price:** USD 119.01

>**#TODO: How much sheet metal?**

[a1rw]:    #custom-parts
[a2rw]:    ../wiring/README.md#main-power-input
[a3mcmc]:  https://www.mcmaster.com/92095A461/
[a4mcmc]:  https://www.mcmaster.com/93625A102/
[a5mcmc]: https://www.mcmaster.com/92095A189/
[a6mcmc]: https://www.mcmaster.com/93475A230/
[a7mcmc]: https://www.mcmaster.com/93625A150/

## Custom parts

### Closure Panel Fabrication
The closure panel is made out of a folded, 1.52mm thick, stainless steel sheet.

| | |
|:------|:-------|
|||

| Download type | Link   |
|:--------------|:-------|
| Fabrication drawing    | [.idw](closure_assembly.idw) [.pdf](closure_assembly.pdf) |
| Source: part CAD model | [.ipt](closure_panel.ipt) |

## Assembly

**Note: Please see general advice in the [manufacturing methods guide](../methods).**

| Download type | Link   |
|:--------------|:-------|
| Engineering drawing        | [.idw](closure_assembly.idw) [.pdf](closure_assembly.pdf) |
| Source: assembly CAD model | [.iam](closure_assembly.iam) |

The main power wire harness `[A2]` terminates with a female 4-pin DIN connector. This connector must be mounted to the
closure panel. Use M2.5 screws `[A3]` and locknuts `[A4]`. Orient the DIN socket with the locking pin facing up.

The main power harness also has a grounding loop that should be used to ground the entire ventilator enclosure.
Us the M4 hardware to secure it at the nearby hole.

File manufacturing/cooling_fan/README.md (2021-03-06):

# Cooling fan

| Outside | Inside |
|:-------------------------:|:-------------------------:|
|  |  |

## Design rationale

Computing electronics and stepper motors generate heat. This heat may accumulate in a closed space. Excess heat
can negatively impact the performance of computer processors and may also pose a fire hazard. A cooling fan
is required to drive hot air out of the enclosure.

**WARNING:** This sub-assembly is current **not functional**.

The first version of the mainboard did not have any provisions for powering and controlling a cooling fan.
Thus, installing one in the current design is simply a proof of concept for the mechanical/manufacturing
design.

Some questions yet to be systematically addressed:
* noise levels
* component lifetime
* air outflow vent
* airflow across the most heat-prone components

## Parts

**Note: If you are a member of the RespiraWorks team, review the [part purchasing guidelines][ppg]
BEFORE purchasing any parts.**

[ppg]: ../purchasing_guidelines.md

| Item  | Quantity | Manufacturer  | Part #                   | Price (USD) | Sources[*][ppg]| Notes |
| ----- |---------:| ------------- | ------------------------ | -----------:|:----------:|:------|
|**A1** | 1        | Noiseblocker  | B0083A0BIA               | 21.86       | [Z][a1amzn] | Cooling fan + guard, 80mm |
|**A2** | 1        | IMSurQltyPrise| 80mm-black-4             | 2.99        | [Z][a2amzn] | Cooling fan filter, 80mm |
|**A3** | 4        | McMaster-Carr | 97763A429                | 1.13        | [C][a3mcmc] | M4 screw, 35mm |
|**A4** | 4        | McMaster-Carr | 93625A150                | 0.06        | [C][a4mcmc] | M4 lock nuts |
|**A5** | 4        | McMaster-Carr | 93475A230                | 0.02        | [C][a5mcmc] | M4 washers, 9mm OD |

**Total assembly price:** USD 29.69

[a1amzn]: https://www.amazon.com/Noiseblocker-NB-BlackSilentPro-PC-P-Ultra-Silent/dp/B0083A0BIA
[a2amzn]: https://www.amazon.com/Computer-Filter-Grills-Aluminum-Stainelss/dp/B07LG41F1K
[a3mcmc]: https://www.mcmaster.com/97763A429/
[a4mcmc]: https://www.mcmaster.com/93625A150/
[a5mcmc]: https://www.mcmaster.com/93475A230/

## Assembly

**Note: Please see general advice in the [manufacturing methods guide](../methods).**

| Assembly | Source |
|:---------|:-------|
| Cooling fan assembly | [.iam](cooling_fan.iam) |

Currently, the fan must be mounted after the internal assembly is already in the enclosure. Because of the
shape of the enclosure, it has been found that the equipment tray must be inserted at an angle. If the cooling
fan were already in place in the enclosure, it would probably interfere with this installation step.

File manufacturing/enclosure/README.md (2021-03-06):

# Enclosure

| Front | Back |
:------------------:|:-----------------:|
|   |   |

## Design rationale

> **TODO:** Content..

## Parts

**Note: If you are a member of the RespiraWorks team, review the [part purchasing guidelines][ppg]
BEFORE purchasing any parts.**

[ppg]: ../purchasing_guidelines.md

| Item  | Quantity | Manufacturer  | Part #                   | Price (USD) | Sources[*][ppg]| Notes |
| ----- |---------:| ------------- | ------------------------ | -----------:|:--------------:|:------|
|**A1** | 1        | RespiraWorks  | [Enclosure panel][a1rw]  | 419.50      | Rw             | Ventilator enclosure, bent sheet metal |
|**A2** | 10       | McMaster-Carr | 97525A415                | 0.09        | [C][a2mcmc]    | 1/8" blind rivets (can also be 3mm) |
|**A3** | 6        | McMaster-Carr | 96439A650                | 0.39        | [C][a3mcmc]    | M4 self-clinching / press-fit nut |
|**A4** | 4        | McMaster-Carr | 96439A710                | 1.21        | [C][a4mcmc]    | M6 self-clinching / press-fit nut |
|**A5** | 4        | McMaster-Carr | 9541K82                  | 0.83        | [C][a5mcmc]    | M6 threaded-stud bumper, used as feet |

**Total assembly price:** USD 430.90

>**#TODO: How much sheet metal?**

[a1rw]:    #custom-parts
[a2mcmc]:  https://www.mcmaster.com/97525A415/
[a3mcmc]:  https://www.mcmaster.com/96439A650/
[a4mcmc]:  https://www.mcmaster.com/96439A710/
[a5mcmc]:  https://www.mcmaster.com/9541K82/

## Custom parts

### Fabrication Drawings

|  |   |
|---|---|
|  |  |
|  |  |

The ventilator enclosure is made up a folded, 1.52mm thick, stainless steel sheet.

| Download type | Link   |
|:--------------|:-------|
| Fabrication Drawing    | [.idw](enclosure.idw) [.pdf](enclosure.pdf) |
| Source: part CAD model | [.ipt](enclosure.ipt) |

## Assembly

**Note: Please see general advice in the [manufacturing methods guide](../methods).**



| Download type | Link   |
|:--------------|:-------|
| Engineering drawing        | [.idw](enclosure.idw) [.pdf](enclosure.pdf) |
| Source: assembly CAD model | [.iam](enclosure_assembly.iam) |

The main panel is folded from a single sheet and fastened together using stainless steel blind rivets. There
are rubber bumper feet on the bottom of the enclosure that are threaded into M6 press-fit nuts. The rubber bumpers
can be removed to allow the enclosure to be mounted to a medical cart.

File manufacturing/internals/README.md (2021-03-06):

# Internal assembly

|  |  |
:------------------:|:-----------------:|
|   |  |

## Design rationale

The internals of the ventilator comprise the main active components of the machine.  To ease assembly and maintainance, they are split into three panels which are designed to be assembled or serviced outside of the enclosure, and then secured into the enclosure as a unit.  The three panels are:
 - **Pneumatics Panel**, described on this page, which hosts the main pneumatic workings of the ventilator: blower, oxygen regulator, control valves, and sensors.
 - **[Display Panel](display_panel)**, which hosts the main electrical workings of the ventilator: touchscreen, controller PCB, and device interfaces.
 - **[Filter Panel](filter_panel)**, which hosts the patient connection fittings and isolation filters.  Air enters and exits the ventilator through this panel.

### Acrylic panels

For serviceability, ventilator internals should be completely removable from the enclosure as a single assembly.
It was necessary to secure front acrylic panels (display panel and filter panel) to the main equipment bracket,
while also allowing it to lay flush with the front face of the enclosure. Heat-set inserts allow the panels to be
mounted securely without obstruction.

The sizing for the mounting holes was based on [this](https://www.pemnet.com/fastening_products/pdf/sidata.pdf) catalog
for heat set inserts. For M4 nuts (page 6, metric table, row 6), length code 1 (5.72 mm) is small enough to fit in the
6.35mm-thick acrylic. The corresponding outer diameter for insertion i.e. acrylic mounting diameter is 5.94 mm.

## Parts

**Note: If you are a member of the RespiraWorks team, review the [part purchasing guidelines][ppg]
BEFORE purchasing any parts.**

[ppg]: ../purchasing_guidelines.md

| Item  | Quantity | Manufacturer   | Part #                               | Price (USD)  | Sources[*][ppg]| Notes |
| ----- |---------:| -------------- | ------------------------------------ | ------------:|:--------------:| ----- |
|**A1** | 1        | RespiraWorks   | [Equipment tray][a1rw]               | 172.13       | Rw             | Metal+acrylic tray holding the internal assembly together  |
|**A2** | 1        | RespiraWorks   | [Filter panel][a2rw]                 | 27.39        | Rw             | Lower front panel assembly with air filters |
|**A3** | 1        | RespiraWorks   | [Blower assembly][a3rw]              | 84.02        | Rw             | Blower sub-assembly |
|**A4** | 1        | RespiraWorks   | [Air check valve][a4rw]              | 21.25        | Rw             | Air check valve sub-assembly |
|**A5** | 2        | RespiraWorks   | [Pinch valves][a5rw]                 | 22.93        | Rw             | Proportional pinch valve sub-assemblies with tubing |
|**A6** | 1        | RespiraWorks   | [Regulator assembly][a6rw]           | 79.12        | Rw             | Oxygen pressure regulator assembly |
|**A7** | 1        | RespiraWorks   | [Proportional solenoid][a7rw]        | 97.44        | Rw             | Proportional solenoid oxygen control valve assembly |
|**A8** | 1        | RespiraWorks   | [Oxygen/overpressure manifold][a8rw] | 131.00       | Rw             | Oxygen sensor and overpressure relief valve manifold |
|**A9** | 1        | RespiraWorks   | [Venturi: air influx][a9rw]          | 2.00         | Rw             | Venturi flow sensor, air influx variant |
|**A10**| 1        | RespiraWorks   | [Venturi: oxygen influx][a10rw]      | 2.00         | Rw             | Venturi flow sensor, oxygen influx variant |
|**A11**| 1        | RespiraWorks   | [Venturi: exhale][a11rw]             | 2.00         | Rw             | Venturi flow sensor, exhale variant |
|**A12**| 1        | RespiraWorks   | [Oxygen mixer][a12rw]                | 1.00         | Rw             | Oxygen mixing chamber |
|**A13**| 1        | RespiraWorks   | [Reducer 3/4"x1/4"][a13rw]           | 1.00         | Rw             | 1/4"ID x 3/4"ID reducer |
|**A14**| 5        | McMaster-Carr  | 53415K153                            | 1.32         | [C][a14mcmc]   | 3/4"ID barbed elbow |
|**A15**| 1        | McMaster-Carr  | 5463K648                             | 0.84         | [C][a15mcmc]   | 3/4"ID x 3/8"ID barbed reducer |
|**A16**| ~1m      | OCSParts       | 117062-5                             | 15.09 / m    | [Z][a16amzn]   | Soft 3/4"ID 1"OD tubing, for main line tubing |
|**A17**| 24       | McMaster-Carr  | 9579K73                              | 0.61         | [C][a17mcmc]   | Herbie clip K (22.2-24.9mm) for clamping 1"OD, main tubing |
|**A18**| 1        | RespiraWorks   | [Display panel][a18rw]               | 601.81       | Rw             | Display panel and electronics assembly |
|**A19**| ~1m      | McMaster-Carr  | 5894K34                              | 7.97 / m     | [C][a19mcmc]   | 1/4"ID 3/8"OD Tygon tubing, for oxygen line tubing |
|**A20**| 6        | McMaster-Carr  | 9579K64                              | 0.50         | [C][a20mcmc]   | Herbie clip BB (9.2-10.3mm) for clamping 3/8"OD, oxygen line tubing |
|**A21**| ~1m      | uxcell         | a16031400ux0163                      | 1.33 / m     | [Z][a21amzn]   | 2.5 mm tubing for connecting venturis to pressure sensors |
|**A22**| 1        | McMaster-Carr  | 2974K392                             | 0.82         | [C][a22mcmc]   | sensing tube 3/23" y-junction, for teeing off to patient pressure sensor |
|**A23**| 1        | RespiraWorks   | [Wiring harnesses][a23rw]            | 9.39         | Rw             | Various wiring assemblies |
|**A24**| 3        | GTSE           | GTSE-10025BLU-USSL                   | 0.04         | [Z][a24amzn]   | Zip ties, for securing sensor tubing and wiring harnesses |

**Total assembly price:** USD 1327.82

[a1rw]:    tray
[a2rw]:    filter_panel
[a3rw]:    blower
[a4rw]:    air_check_valve
[a5rw]:    pinch_valve
[a6rw]:    regulator
[a7rw]:    PSOL
[a8rw]:    manifold
[a9rw]:   venturi
[a10rw]:   venturi
[a11rw]:   venturi
[a12rw]:   mixer
[a13rw]:   reducer_3-4_1-4
[a14mcmc]: https://www.mcmaster.com/53415K153/
[a15mcmc]: https://www.mcmaster.com/5463K648
[a16amzn]: https://www.amazon.com/gp/product/B01LZ5ZK53
[a17mcmc]: https://www.mcmaster.com/9579K73
[a18rw]:   display_panel
[a19mcmc]: https://www.mcmaster.com/5894K34
[a20mcmc]: https://www.mcmaster.com/9579K64
[a21amzn]: https://www.amazon.com/gp/product/B01F4BJ7PI
[a22mcmc]: https://www.mcmaster.com/2974K392
[a23rw]:   ../wiring
[a24amzn]: https://www.amazon.com/GTSE-Small-Strength-Nylon-Cable/dp/B086H4TR5Y

## Assembly

**Note: Please see general advice in the [manufacturing methods guide](../methods).**

[Pneumatics assembly model](internals.iam)

The rough order/hierarchy of internals assembly is as follows:

1. Assemble the [equipment tray](tray) which will hold everything else
2. Install the [filter panel](filter_panel) to the equipment bracket
3. Install the [blower assembly](blower) onto the pneumatics tray
4. Attach the [air check valve](air_check_valve) to the blower assembly
5. Install 2x [Pinch valves](pinch_valve), for air influx and exhale control
    * remember to label the pinch valve wiring "inhale" and "exhale" appropriately
6. Install the [oxygen regulator assembly](regulator)
7. Install the [proportional solenoid](PSOL) valve for oxygen control

| Step 1                    | Steps 2-7                 |
|:-------------------------:|:-------------------------:|
|  |  |

8. Install the main tubing, sensors and manifolds:
    * [Manifold](manifold) - for oxygen sensor and overpressure relief valve
    * [Oxygen mixer](mixer) - for mixing air and oxygen before delivery to patient
    * [Venturi flow sensors](venturi) - in-house design of affordable flow sensors
    * Various tubing adapters `[13-15]`
    * 3/4 tubing `[16]` and clamps `[17]`
9. Install the [display panel](display_panel)
10. Install oxygen line tubing `[A19]` and clamps `[20]`

| Step 8                    | Steps 9-10 (except clamps) |
|:-------------------------:|:--------------------------:|
|  |   |

### Sensor tubing

Sensor tubing `[A21-22]` connects the venturis to pressure sensors in the electronics assembly.

The tubes you will use will vary in length. Use your own discretion.

Use the following principles to guide this process:
* The venturis have arrows embossed on the sides indicating flow direction. You can thus determine which of the two
  sensor ports is "upstream" vs. which one is "downstream".
* The differential sensors on the PCB (or daughter-card) have 2 ports each:
  * the upper port (further from board) is for upstream
  * the lower port (closer to board) is for downstream

Connect the tubing as follows
* upstream port on the `air influx venturi` to upper port on the `INHALE FLOW` sensor on the PCB
* downstream port on the `air influx venturi` to lower port on the `INHALE FLOW` sensor on the PCB
* upstream port on the `oxygen influx venturi` to upper port on the pressure sensor on the daughter-card
* downstream port on the `oxygen influx venturi` to lower port on the pressure sensor on the daughter-card
* downstream port on the `exhale venturi` to lower port on the `EXHALE FLOW` sensor on the PCB
* upstream port on the `exhale venturi` to wye splitter `[A22]`
* wye splitter `[A22]` to the upper port on the `PATIENT PRESSURE` sensor on the PCB
* wye splitter `[A22]` to the upper port on the `EXHALE FLOW` sensor on the PCB
* the lower port on the `PATIENT PRESSURE` sensor remains open to atmosphere

| Air influx                     | Oxygen influx                  | Outflow and patient pressure   |
|:------------------------------:|:------------------------------:|:------------------------------:|
|  |  |  |

### Final wiring

By this point you should have completed all the mechanical and pneumatic sub-assemblies of the ventilator.

You can now connect all the wiring (except main power):
* connect blower power wires to PCB
* connect blower control wires
  * to the interim board, if you have one
  * else, to the PCB
* connect proportional solenoid to PCB
* connect oxygen sensor to interim board
* connect the pinch valves to their driver pigtails as follows:
  * top - inhale
  * bottom - exhale
* Secure wiring with zip ties `[A24]`
* Secure sensor tubing with zip ties `[A24]`, but do so lightly. Don't tighten them to the point where the
  air flow is restricted in the tubes or where the wires can't move at all.

| Top view          | Bottom view       |
:------------------:|:-----------------:|
|  |  |

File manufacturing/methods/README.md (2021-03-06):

# Manufacturing methods

Since we have to manufacture some custom components for the prototypes, it is worth trying to do so in as
reproducible a way as possible, so that we are testing (even in the prototyping phase) with components of similar
properties. Secondarily, this should help everyone get started faster and avoid having to reinvent the wheel.

**DISLAIMER:** None of the following constitutes an endorsement of the listed products. We have done no systematic
comparative study of alternate products and have no evidence to indicate that the following are the most appropriate
for any particular purpose.

**Note: If you are a member of the RespiraWorks team, review the [part purchasing guidelines][ppg]
BEFORE buying any parts.**

[ppg]: ../purchasing_guidelines.md

Below you will find advice on the following:
* [Sheet metal](#sheet-metal)
* [3d Printing](#3d-printing)
* [Gaskets](#gaskets)
* [Heat set inserts](#heat-set-inserts)
* [Acrylic panels](#acrylic-panels)
* [Flexible tubing](#flexible-tubing)
* [Tapered thread connectors](#tapered-threads)
* [Screwdrivers and hand taps](#screwdrivers)

## Sheet metal

**Hazard:** sheet metal edges may be sharp and you could hurt yourself while working with these components.
It is highly advise that you deburr, file and/or send all edges before you do any work with sheet metal parts.

## 3d Printing

We have been printing quite a few custom pneumatics and mechanical components. The following is a summary of what has
worked.

### Printers

We have been printing with SLA printers, such as:

* [Anycubic Photon](https://www.anycubic.com/collections/anycubic-photon-3d-printers/products/anycubic-photon-3d-printer)
* [Elegoo Mars](https://www.elegoo.com/collections/mars-series)

### Resin

We have been using either:
* [SirayaTech Fast](https://www.amazon.com/ABS-Like-Curing-Non-Brittle-Printing-Resin/dp/B07WFJ53LP) ABS-like resin
  (comes in various colors)
* The above mixed with ~30% [SirayaTech Tenacious](https://www.amazon.com/Tenacious-Flexible-Resistant-Siraya-Tech/dp/B07PLJ9XW9)
  to mitigate brittleness
  * If you have problems with parts cracking from impacts, try this mix.  It strong but slightly flexible, which makes
    it resistant to cracking.
  * The densities are similar so it doesn't matter too much if you mix it by mass or volume.  If you have a scale, you
    can mix it by mass right in the bottle, and this may reduce mess.
* [SirayaTech Clear V2](https://www.amazon.com/Blu-Strong-Precise-Resolution-Printing/dp/B083DLSR1W) Nearly transparent,
  but harder to print with. Good for things like filter housings that need to look good but don't require precision
  and strength.

Guides for printing and curing are provided on the [manufacturer's website](https://siraya.tech/pages/support).

### Slicing

Software included with lower-end SLA printers may not be the most up-to-date. We have found it useful to scaffold and
slice the models using [ChituBox](https://www.chitubox.com/). It is available for free and runs on most operating
systems, including Linux.

The following are configuration profiles we have used in Chitubox for some of the above-mentioned printer-resin combinations:
* [Anycubic Photon & Fast resin](AnyCubic_Photon_Siraya_fast_profile.cfg)
* [Anycubic Photon & 70:30 Fast:Tenacious blend](AnyCubic_Photon_Fast7_+_tenacious3_profile.cfg)
* [Anycubic Photon & Blu Clear 2 resin](AnyCubic_Photon_Siraya_Blu_Clear_2_profile.cfg)
* Elegoo Mars & Fast Resin: the default settings in Chitubox for Printer: "Elegoo Mars" and Resin: "Elegoo Standard Resin Grey for 0.05mm" work perfectly.
* [Elegoo Mars & 70:30 Fast:Tenacious blend](Elegoo_Mars_70fast_30tenacious_profile.cfg)
  * This is exactly the same as the Elegoo Standard Grey resin profile, except with lifting speed reduced to 60mm/min to prevent layer separation issues.

There is a page with additional advice on using Chitubox with the Anycubic Photon printer
[here](https://all3dp.com/2/chitubox-anycubic-photon-settings-profile/).
The Elegoo Mars works natively with chitubox.

### Kind request

When you print a new part, you may customize the scaffolding which provides some improvement over the defaults. If you
have used Chitubox to do this, please save a `*.chitubox` of your intermediate object before slicing, and upload this
file to share with others. This will save everyone time and, again, improve consistency across the team. You may
also provide whatever final printer-specific files, such as `*.photon`.

Please:
* reference version of CAD model that was rendered for printing
* add any new binary file types to be tracked by [git LFS](https://github.com/RespiraWorks/Ventilator/wiki#adding-new-binary-files).

### Post-printing finishing

For finer pieces that require tighter fits and smoother edges, you might find it useful to have
a set of [needle files](https://www.grainger.com/product/23N602).

## Gaskets

For cutting gaskets, you can use a
[craft knife](https://www.amazon.com/Fiskars-167110-1001-Heavy-Craft-Knife/dp/B001A42CTW).

## Heat set inserts

A number of components may have to be mounted using heat-set inserts in lieu of nuts. These may go into
either acrylic of 3d-printed parts. The following describes how to install them.

First off, you will need a soldering iron. It need not be an expensive one you would use for assembling electronics.
In fact, you should prefer a bulkier one, such one used for wood-burning crafts, such as
[this](https://www.amazon.com/Walnut-Hollow-Versa-Temp-Temperature-Woodburning/dp/B005P1TRAS).

1. Select a soldering iron tip large enough to provide uniform pressure on the center of the heat-set insert, but small
   enough to not touch the surrounding material.
2. Heat up your soldering iron to an operating temperature of around 343-399&deg;C (650-750&deg;F).
3. Place the heat-set insert into the mounting hole with the smaller diameter facing down into the hole away from you.
4. Touch the tip of the soldering iron to the top of the heat-set insert and wait for a few seconds.
5. The weight of the soldering iron should gently push the heat-set insert into the now melted plastic.
6. Press down slowly until the half the heat-set insert inserted into the plastic. At this point only the first set of
   knurls should be inside the plastic.
7. Allow the plastic to cool. Then push inserts in all the way till it is flush with the face of the plastic.
8. Remove heat and allow to cool and harden.

Works best if you push each of the inserts you are working on halfway, let them cool and come back to finish
them in turn.

| Start (step 4)             | Half-way (step 6)           |
|:--------------------------:|:---------------------------:|
| |  |

## Acrylic panels

We have a number of acrylic panels in the enclosed prototype. Clear acrylic was partly chosen because it
can be easily modified while quickly iterating our design, certainly more easily than any metal components.

Ideally, acrylic panels should be cut by laser. They can be cut precisely to specification.

>*TODO:* add section on laser cutters, settings, etc..

### Acrylic and hand-tools

You may not have access to a laser cutter. Or you may need to make a quick modification that does not warrant
creating a whole new CAD model and producing a part from scratch.

Common woodworking tools are perfectly adequate for modifying acrylic panels. Some of the following might be useful:

| Item   | Manufacturer   | Part #             | Price (USD)  | Sources[*][ppg] | Notes |
| ------ | -------------- | -------------------| ------------:|:---------------:|:------|
| **B1** | Black & Decker | BDEJS300C          | 24.49        | [A][b1amzn]     | Jigsaw, for cutting acrylic |
| **B2** | Black & Decker | BDEDMT             | 29.99        | [A][b2amzn]     | Electric hand drill, **drill press preferred if you have one**, for drilling acrylic |
| **B3** | XLCMSY         | EAN: 0742880496381 | 12.99        | [A][b3amzn]     | Cobalt metric drill bits, in particular - 4.5mm |
| **B4** | Porter Cable   | PC1014             | 59.59        | [A][b4amzn]     | Forstner bits, **preferred for drill press** |
| **B5** | KATA TOOLS     | KTL89020           | 19.99        | [A][b5amzn]     | Hole saws, **preferred for hand drill** |

[b1amzn]: https://www.amazon.com/BLACK-DECKER-Jig-Amp-BDEJS300C/dp/B00OJ72L84
[b2amzn]: https://www.amazon.com/BLACK-DECKER-BDEDMT-Matrix-Driver/dp/B0094B9BHE
[b3amzn]: https://www.amazon.com/XLCMSY-Straight-Resistant-Stainless-1-5-6-5mm/dp/B07ZQGXWGL
[b4amzn]: https://www.amazon.com/PORTER-CABLE-PC1014-Forstner-Bit-14-Piece/dp/B004TSZEB4
[b5amzn]: https://www.amazon.com/KATA-19-152mm-Mandrels-Installation-Plywood/dp/B08JCHY2DM

You might also want to use some 200 grit sandpaper to clean up the edges of the pieces you cut and drill.

## Flexible tubing

We have been using various types of rubber, silicon and Tygon tubing. Not all cut easily with the same type of tools.
Sometimes a [PVC pipe cutter](https://www.amazon.com/gp/product/B07Y997XKC) has worked well, other times - household
scissors or a sharp knife will do.

You may have to clamp tubing to barbed fittings, or you may want to remove the clips so that you can remove the tubing.
These [self-adjusting pliers](https://www.amazon.com/gp/product/B008S0FVWG) have proven themselves useful for either
task.

## Tapered threads

Use PTFE tape ([McMaster](https://www.mcmaster.com/6802K11/) or [Amazon](https://www.amazon.com/gp/product/B01L2F428C))
on all tapered thread joints, such as NPT. The tape not only ensures a tighter seal, but also makes it go in easier and
prevents it from seizing up if you do eventually need to remove the part.

Make sure you wrap it in the same direction as the threads will go in. There are videos online on how
to do this correctly.

You may need an [adjustable wrench](https://www.amazon.com/GETUPOWER-10-Inch-Adjustable-Opening-Vanadium/dp/B07RGV2VK1)
as well, though depending on the type of fitting you are attempting to thread pliers might also work.

## Screwdrivers

Most of the screws in the ventilator assembly require a metric hex-shaped driver.

If you already have some sort of socket driver, you could just get some
[metric hex bits](https://www.amazon.com/Wiha-71397-Metric-Insert-6-Piece/dp/B0084B7S70).

If you got nothing, a cheap choice would be a set of
[hex key wrenches](https://www.amazon.com/TEKTON-Wrench-Metric-30-Piece-25253/dp/B00I5TH074).

For something more comfortable and versatile, you could also go with a
[precision screw driver set](https://www.amazon.com/gp/product/B07R9VTWG5).

There may be a few components that require tapping or chasing of printed threads. The dedicated parts pages
will hopefully identify the exact type of tap you need. However, you may need a handle to operate these taps.

Something like [this set](https://www.amazon.com/gp/product/B003GKJYKI) should be able to handle the range of diameters
of the taps listed.

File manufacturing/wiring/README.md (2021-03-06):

# Wiring assemblies

The following page describes the custom wiring components required in the electrical assembly. Manufacturing
these components will require soldering and crimping.

For a single ventilator unit, the following custom wiring assemblies are needed:
* [Main power](#main-power-input)
* [Blower power](#blower-power)
* [Blower signal/control](#blower-control-cable)
* [Stepper motor pigtails (x2)](#stepper-wiring)
* [Proportional solenoid](#proportional-solenoid-valve)
* [Oxygen sensor](#oxygen-sensor-cable)

It is probably a good idea to manufacture and test these before proceeding with the rest of the mechanical assembly.

Total price estimate: USD 24.00

Stand-alone items (not in other assemblies): USD 9.39

## Parts

**Note: If you are a member of the RespiraWorks team, review the [part purchasing guidelines][ppg]
BEFORE purchasing any parts.**

[ppg]: ../purchasing_guidelines.md

| Item  | Quantity | Manufacturer  | Part #                | Price (USD)  | Sources[*][ppg]      | Notes |
| ----- |---------:| ------------- | --------------------- | ------------:|:--------------------:| ----- |
|**A1** | 20       | JST           | SXH-001T-P0.6         |         0.10 | [K][a1key]           | XH crimp contacts, for sensor & actuator connections |
|**A2** | 1        | JST           | XHP-2                 |         0.10 | [K][a2key]           | XH 2-pin housings, for solenoid |
|**A3** | 1        | JST           | XHP-3                 |         0.10 | [K][a3key]           | XH 3-pin housings, for oxygen sensor |
|**A4** | 1        | JST           | XHP-6                 |         0.12 | [K][a4key]           | XH 6-pin housings, for blower control |
|**A5** | 7        | JST           | SVH-21T-P1.1          |         0.11 | [K][a5key] [R][a5rs] | VH crimp contacts, for main power, for blower power |
|**A6** | 2        | TE            | 1-1123722-2           |         0.18 | [K][a6key] [R][a6rs] | VH housing 2 pin, for blower power |
|**A7** | 1        | JST           | VHR-3N                |         0.14 | [K][a7key]           | VH housing 3 pin, for main power |
|**A9** | 1        | Kycon         | KPJX-PM-4S            |         2.89 | [K][a9key]           | 4 pin DIN female, main power connector |
|**A10**| 8        |TE Connectivity| 102107-3              |         0.47 | [K][a10key]          | 2.54mm male pin, for stepper interface |
|**A11**| 2        |TE Connectivity| 87499-7               |         0.73 | [K][a11key]          | 2.54mm 4-pin housing, for stepper interface |
|**A12**| ~2.5 m   | Remington     | 16UL1007STRKIT        |  0.66 / m    | [Z][a12amzn]         | 16 AWG wire, for power cables |
|**A13**| ~1.5 m   | Remington     | 22UL1015STRKIT10COLOR |  0.50 / m    | [Z][a13amzn]         | 22 AWG wire, for signal/control cables |
|**A14**| ~4 m     | Remington     | 26UL1007STRKIT10COLOR |  0.42 / m    | [Z][a14amzn]         | 26 AWG wire, for signal/control cables |
|**A15**| (1)      | WGCD          | 4330589508            |         8.99 | [Z][a15amzn]         | XH connector kit for 2/3/4/5 pins, **alternative for A1-3** |
|**A16**| (1)      | CQRobot       | CQRJST254-BGB         |         9.99 | [Z][a16amzn]         | XH connector kit for 6/7/8 pins, **alternative for A1 and A4** |
|**A17**| (1)      | Chenbo        | WJ-Z01                |        11.98 | [Z][a17amzn]         | 2.54mm connector kit, **alternative for A10 and A11** |
|**A18**| 2        | Molex         | 22013037              |         0.20 | [K][a18key]          | KK-series 3-pin sockets connector housing (oxygen sensor) |
|**A19**| 4        | Molex         | 08550102              |         0.21 | [K][a19key]          | crimp sockets for the above |
|**A20**| ~1 m     | uxcell        | a11110900ux0059       | 1.32 / m     | [Z][a20amzn]         | Shrink tubing, black, 3mm diameter |
|**A21**| ~2 m     | uxcell        | A17032300ux0991       | 1.50 / m     | [Z][a21amzn]         | Shrink tubing, black, 4mm diameter |
|**A22**| ~0.5 m   | XHF           | B07WC9BGRT            | 0.95 / m     | [Z][a22amzn]         | Shrink tubing, red, assorted diameters |
|**A23**| 1        |Phoenix Contact| 3240078               | 0.15         | [K][a23key]          | M4 ring terminal, 14-18AWG |

[a1key]:   https://www.digikey.com/short/z44f8d
[a2key]:   https://www.digikey.com/short/z44f8f
[a3key]:   https://www.digikey.com/short/z44fb9
[a4key]:   https://www.digikey.com/short/z44ff8
[a5key]:   https://www.digikey.com/short/z44fjr
[a5rs]:    https://export.rsdelivers.com/product/jst/svh-41t-p11/jst-nv-vh-female-crimp-terminal-contact-16awg-svh/7620692
[a6key]:   https://www.digikey.com/short/z44fwj
[a6rs]:    https://export.rsdelivers.com/product/jst/vhr-2n/jst-vhr-female-connector-housing-396mm-pitch-2/8201172
[a7key]:   https://www.digikey.com/short/z44fwp
[a9key]:   https://www.digikey.com/en/products/detail/kycon-inc/KPJX-PM-4S/9990081
[a10key]:  https://www.digikey.com/en/products/detail/te-connectivity-amp-connectors/102107-3/298993
[a11key]:  https://www.digikey.com/en/products/detail/te-connectivity-amp-connectors/87499-7/29911
[a12amzn]: https://www.amazon.com/gp/product/B00N51OJJ4
[a13amzn]: https://www.amazon.com/gp/product/B073SDGNKW
[a14amzn]: https://www.amazon.com/gp/product/B011JC76OA
[a15amzn]: https://www.amazon.com/gp/product/B06ZZ45G7G
[a16amzn]: https://www.amazon.com/gp/product/B079MJ1RYN
[a17amzn]: https://www.amazon.com/CHENBO-Connector-Housing-Assortment-Terminal/dp/B077X8XV2J
[a18key]:  https://www.digikey.com/en/products/detail/molex/0022013037/26433
[a19key]:  https://www.digikey.com/en/products/detail/molex/0008550102/172056
[a20amzn]: https://www.amazon.com/uxcell-Polyolefin-Insulation-Shrink-Tubing/dp/B008DFW8JA
[a21amzn]: https://www.amazon.com/uxcell-4mm-Shrink-Sleeve-Tubing/dp/B071VGQH97
[a22amzn]: https://www.amazon.com/XHF-140-PCS-Red-Wear-Resistant/dp/B07WC9BGRT
[a23key]:  https://www.digikey.com/en/products/detail/phoenix-contact/3240078/4458695

## Tools

| Item | Manufacturer | Part number         | Price($) | Sources[*][ppg] | Notes |
| ---- | ------------ | ------------------- | --------:|-----------------| ----- |
| B1   | Preciva      | PR-3254 (PR102001)  |    39.99 | [Z][b1amzn]     | Crimping tool (with connector kit) |
| B2   | NovelLife    | TS100               |    74.99 | [Z][b2amzn]     | 65W Soldering iron kit |
| B3   | Chandler     | HG603D              |    24.92 | [Z][b3amzn]     | Heat gun, for shrink tubing |
| B4   | Kester       | KE1107-ND           |    58.98 | [K][b4key]      | Solder |

[b1amzn]: https://www.amazon.com/gp/product/B07R1H3Z8X
[b2amzn]: https://www.amazon.com/NovelLife-Mini-TS100-Soldering-Digital/dp/B07D35B75T
[b3amzn]: https://www.amazon.com/Chandler-Tool-Embossing-Heat-Gun/dp/B07GC5N3QC
[b4key]:  https://www.digikey.com/en/products/detail/kester-solder/24-6040-0010/265622

**Crimper Tips:**

* Position 1 on the crimper will crimp JST XH contacts `[A1]` and Molex KK contacts `[A19]`
* Position 2 on the crimper will crimp VH contacts `[A5]`.  However, with certain gauges of wire, this crimper may bend the contact into a shrimp-like shape.  If this happens, bend the contact back straight (it should be pretty obvious as it blocks insertion)
* Position 3 on the crimper will crimp 2.54mm (aka Dupont) sockets and pins `[A10]`.
* A proper crimp should crimp the insulation in the lower half and the wire in the upper half of the crimp portion of the contact.
* The crimper kit `[B1]` comes with a lot of XH contacts, but not any VH contacts.

## Assembly

**Note: Please see general advice in the [manufacturing methods guide](../methods).**

As much as possible we should try to keep the cables one-to-one
(for example the wiring of the PCB to blower driver cables are all pin 1 to pin 1,
pin 2 to pin 2, etc. with the same connector style on both ends.

### Main power input

You will need all the tools listed.

* Using:
  * DIN female receptacle `[A9]`
  * 16AWG wire 65mm each in black and red `[A12]`
  * 2x VH crimp contacts `[A5]`
  * VH 3-pin housing `[A7]`
  * Shrink tubing `[A20-22]`
  * 16AWG wire green, 30 cm `[A12]`
  * M4 ring terminal `[A23]`

- Instructions:
  - Cut two 5cm lengths from each of the wire colors.
  - Solder the 5cm lengths to the 4-pin Power DIN connector per the drawing below. It will be easier if you use a hot iron (>370C) and you pre-tin both the wires ends and the connector solder cups.
  - Apply heat shrink to the 4 exposed connections.
  - Solder the two black wires to the remaining length of the black wire, and do the same with the red.  Apply heat shrink to the junction.
  - Slide on a few extra lengths of heat shrink tubing for cable management before you proceed.
  - Crimp the VH contacts onto the ends of the red and black wire, then push them into the housings according to the drawing until they click.
  - Do a gentle pull test to confirm proper seating of the contact.
  - Shrink the remaining pieces of heat shrink to make the cable more manageable.

- Enclosure grounding terminal (process image 4):
  - solder two 10cm lengths of green wire to the sides of the DIN connector (which can remain exposed)
  - solder the two pieces of green wire together and to the remaining 10 cm length
  - apply some shrink tubing to where the three wires meet
  - crimp the ring terminal to the end of the wire

- Total price: USD 8.61

| Cable Image | Cable Drawing (PDF)  |
|:--------:|:--------:|
| Main Power Input Cable | Main Power Input Cable Drawing |

| Process Image 1 | Process Image 2  | Process Image 3 | Process Image 4 |
|:--------:|:--------:|:--------:|:--------:|
| Process Image 1 | Process Image 2 | Process Image 1 |  Process Image 1 |

### Blower power

The power cable that comes included with the blower will be too short to reach the PCB,
so a new one must be manufactured.

* Using:
  - 16AWG 50cm in each of black and red `[A12]`
  - 4x VH crimp contacts `[A5]`
  - 2x VH 2-pin housings `[A6]`
  - Shrink tubing `[A21]`

- Instructions:
  - Crimp the VH contacts onto one end of each of the wires.
  - Slide on a few extra lengths of heat shrink tubing for cable management before you proceed.
  - Crimp the VH contacts onto the other end of the wires.
  - Push the contacts into the housings per the drawing until they click.
  - Do a gentle pull test to confirm proper seating of the contact.
  - Shrink the remaining pieces of heat shrink to make the cable more manageable.

- Total price: USD 2.87

| Cable Image | Cable Drawing (PDF)  |
|:--------:|:--------:|
| Blower Power Cable | Blower Power Cable Drawing |

### Blower control cable

The signal cable that comes included with the blower will be too short to reach the PCB,
so a new one must be manufactured.

* Using:
  - 26AWG 50cm each of 6 different colors `[A14]`
  - 12x XH crimp contacts `[A1]`
  - 2x XH 6-pin housings `[A4]`
  - Shrink tubing `[A21]`

- Instructions:
  - Crimp the XH contacts onto one end of each of the wires.
  - Slide on a few extra lengths of heat shrink tubing for cable management before you proceed.
  - Crimp the XH contacts onto the other end of the wires.
  - Push the contacts into the housings per the drawing until they click.
  - Do a gentle pull test to confirm proper seating of the contact.
  - Shrink the remaining pieces of heat shrink to make the cable more manageable.

- Total price: USD 3.45

| Cable Image | Cable Drawing (PDF)  |
|:--------:|:--------:|
| Blower Control Cable | Blower Control Cable Drawing |

### Stepper wiring

To power and control the pinch valves, they will need to be wired to the stepper driver boards. Two pigtails
can be produced for this purpose:

Recipe for one pigtail:
* 4x 22AWG 15cm `[A13]`
* 4x male 2.54mm crimp pins `[A10]`
* 2.54mm 4-pin housing `[A11]`

On the other end, each wire should be stripped about 5mm and solder applied to bind the threads.

It is advisable to label these pigtails to identify which stepper driver they shall be wired up to.
The same can be done for the stepper motors belonging to each pinch valve assembly.

Single pigtail price: USD 3.00

| Pigtails | Stepper wires  |
|:--------:|:--------:|
|  |  |

You will also need 2x small (about 5cm) 16AWG wires for connecting the two stepper boards together for power.

### Proportional solenoid valve

To connect the solenoid to the PCB, you will need to crimp a 2-pin XH connector to the wires.

- Using:
  - 2x XH crimp contacts `[A1]`
  - XH 2-pin housings `[A2]`
  - Shrink tubing `[A20]`

- Instructions:
  - Note that the polarity of these connections does not matter.
  - Slide a few extra lengths of heat shrink tubing onto the solenoid wires for cable management before you proceed.
  - Crimp the XH contacts onto the other end of the wires.
  - Push the contacts into the housings per the drawing until they click.
  - Do a gentle pull test to confirm proper seating of the contact.
  - Shrink the remaining pieces of heat shrink to make the cable more manageable.

- Total price: USD 0.96

| Cable Image | Cable Drawing (PDF)  |
|:--------:|:--------:|
| Proportional Solenoid Cable | Proportional Solenoid Cable Drawing |

### Oxygen Sensor Cable

This cable connects the Oxygen Sensor to the Interim Board in the PCB stack.

- Using:
  - 26AWG 40cm in each of green and white `[A14]`
  - 4x KK series crimp contacts `[A19]`
  - 2x KK series 3-pin housings `[A18]`
  - Shrink tubing `[A20]`

- Instructions:
  - Strip the ends of the wires
  - Using the crimper `[B1]` in position 1, crimp 4x contacts `[A19]` onto the ends of the wires.
  - Sheathe the length of the wires in 3mm shrink tubing `[A20]` before inserting the ends into housing.
  - Insert the wires into the connector housings `[A18]`, according to the drawing, until they click.  Pin 1 is marked by a tiny '1' molded into the connector housing.
  - Do a gentle pull test to make sure that the contacts are properly crimped and seated.

- Total price: USD 2.11

| Cable Image | Cable Drawing (PDF)  |
|:--------:|:--------:|
| Oxygen Sensor Cable | Oxygen Sensor Cable Drawing |

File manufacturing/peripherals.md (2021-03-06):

# Peripheral components

These components are not stricly part of the ventilator assembly, but they may be necessary to get the prototype to
work. The most obvious of these would be the power supply cables. Other devices might also be needed depending on
how you intend to deploy software, test and control the prototype.

## Parts

**Note: If you are a member of the RespiraWorks team, review the [part purchasing guidelines][ppg]
BEFORE purchasing any parts.**

[ppg]: purchasing_guidelines.md

| Item | Quantity | Manufacturer  | Part Number        | Price (USD) | Sources[*][ppg]         | Notes |
| ---- |---------:| --------------| ------------------ | -----------:|:-----------------------:| ----- |
|**A1**| 1        | Mean Well     | GSM160A12-R7B      | 63.99       | [K][a1key]              | 12v Power supply adapter, medical grade, 11.5A |
|**A2**| 1        | Cablelera     | ZWACPCAY-10        | 8.99        | [Z][a2amzn]             | Hospital grade power cord |
|**A3**| (1)      | Anker         | 68ANREADER-B2A     | 12.99       | [Z][a3amzn]             | microSD-USB adapter, for flashing RasPi images |
|**A4**| (1)      | Monoprice     | 3896               | 0.83        | [Z][a4amzn] [O][a4mono] | USB-A to miniUSB-B cable, for programming the nucleo |
|**A5**| (1)      | VicTsing      | IC192305US         | 23.99       | [Z][a5amzn]             | Wireless keyboard and mouse, for setting up Rpi, **OPTIONAL** |

**Essentials (A1+A2):** USD 72.98

[a1key]:  https://www.digikey.com/en/products/detail/mean-well-usa-inc/GSM160A12-R7B/7703457
[a2amzn]: https://www.amazon.com/Cablelera-North-American-Hospital-ZWACPCAY-10/dp/B00GP6CB5A
[a3amzn]: https://www.amazon.com/Anker-Portable-Reader-RS-MMC-Micro/dp/B006T9B6R2
[a4amzn]: https://www.amazon.com/AmazonBasics-USB-2-0-Cable-Male/dp/B00NH13S44/
[a4mono]: https://www.monoprice.com/product?p_id=3896
[a5amzn]: https://www.amazon.com/VicTsing-Keyboard-Adjustable-Independent-Indicator/dp/B07TT3VN4X

### Power

Once the ventilator is assembled, you may use `[A1]` and `[A2]` power it.

You may also want to use `[A4]` to connect the controller to your PC from which you will be flashing
controller firmware.

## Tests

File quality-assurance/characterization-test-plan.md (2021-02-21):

# Characterization Test Plan

This document will track desired characterization tests and link to the corresponding data when the test is performed.
Eventually the info from this document will likely be formalized into a record of tests that have been performed as part
of the development and validation of the ventilator - integration tests with the real software are expected to be
defined elsewhere, though they could be folded into this.

**Caution:** this document has not been formally reviewed and is a work in progress. Be responsible to understand the
provenance of documentation.

**NOTE:** these tests are supposed to be iteratively developed. As we progress, the tests will become more granular.

## System Characterization

* **Fan Tests**

**#TODO** Add content

[View fan tests](../manufacturing/internals/blower/characterization-tests)

* **PIP/PEEP/Timing Tests**

    1. What is the maximum pressure that can be achieved with the current blower with a representative amount of tubing, a fully open air inhale valve, and a fully closed exhale valve?

    2. From PEEPs of 0 to 20 cm H20 (in reasonable increments), how quickly can the current design achieve PIPs from 10 cm H20 up to 60 cm H20 (or the max value, testing reasonable increments)?

    3. From PIPs from 20 cm H20 up to 60 cm H20 (or however high can be achieved, in reasonable increments), how quickly can the system vent down to PEEPs of 0 to 20 cm H20 (testing reasonable increments)?

    4. For PIPs from 20 cm H20 up to 60 cm H20 (in reasonable increments), what is the maximum flow rate into the patient that can be achieved? How does this change as a function of how much the exhaust valve is open?

    5. For 1-4 with a flow source that is better than the blower, what can be achieved (what becomes the next lim fac)?

* **System Sensitivity Tests**

    1. What is the difference in pressure right after the inhale venturi (before the humidifier) and at the patient pressure sensor before the exhale venturi?

## Valve Tests

* **Pinch Valve Characterization**

    1. How quickly can the pinch valve be fully opened? How does this change as a function of pressure (up to at least 60 cm H20)?

    2. How quickly can the pinch valve be fully closed? How does this change as a function of pressure (up to at least 60 cm H20)

    3. What is the leak rate past a fully closed pinch valve as a function of pressure (up to at least 60 cm H20)?

* **Proportional Solenoid Characterization**

    1. How quickly can the solenoid be fully opened? How does this change as a function of pressure (up to at least 60 cm H20)?

    2. How quickly can the solenoid be fully closed? How does this change as a function of pressure (up to at least 60 cm H20)

    3. What is the leak rate past a fully closed solenoid valve as a function of pressure (up to at least 60 cm H20)?

## Sensor Tests

* **DP sensor/Venturi characterization**

    1. For flow rates from 1 to 80 lpm, how accurate is the flow measurement and how does this accuracy change over time (if sitting at a specific FiO2)?

    2. How do the measurements for letter i above change as a function of temperature and humidity?

    3. How do the measurements for letter i above change as a function of the flow rate that is being started at (e.g. if you go from 1->80 or 40->80 does the accuracy change? What about 80->1 and 80->40)?

    4. When there is a change in flow rate, how long does it take for the sensor to settle?

    [View Venturi tests](../manufacturing/internals/venturi/characterization-tests/06072020/README.md)

* **Pressure sensor characterization**

    1. For pressures from 1 to 60 cm H20, how accurate is the pressure reading and how does this accuracy change over time (if sitting at a specific FiO2)?

    2. How do the measurements for letter i above change as a function of temperature and humidity?

    3. How do the measurements for letter i above change as a function of flow rate past the sensor?

    4. How do the measurements for letter i above change as a function of the pressure that is being started at (e.g. if you go from 5->60 or 30->60 does the accuracy change? What about 60->5 and 60->30)?

    5. When there is a change in pressure, how long does it take for the sensor to settle?

* **O2 sensor characterization**

    1. For FiO2s from 21% to 100%, how accurate is the o2 sensor reading and how does this accuracy change over time (if sitting at a specific FiO2)?

    2. How do the measurements for #1 change as a function of temperature and humidity?

    3. How do the measurements from #1 change as a function of flow rate?

    4. When there is a change in FiO2, how long does it take for the sensor to settle?

## Things that need to be added

* #todo Add electronics/Software/Controller tests?

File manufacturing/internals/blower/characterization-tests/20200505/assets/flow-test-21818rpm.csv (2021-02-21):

t | p1_adc | patient | p2_adc | p2 | p3_adc | p3 | Q1
0.05 | 457.0 | 1.186104218362283 | 580.0 | 1.7855361596009975 | 629.0 | 2.0150753768844223 | 66.27393128634002
0.1 | 448.0 | 1.1414392059553349 | 632.0 | 2.0448877805486285 | 663.0 | 2.185929648241206 | 70.92398808883199
0.15 | 480.0 | 1.3002481389578164 | 557.0 | 1.6708229426433916 | 641.0 | 2.0753768844221105 | 64.109682099571
0.2 | 461.0 | 1.205955334987593 | 638.0 | 2.0748129675810474 | 600.0 | 1.8693467336683418 | 71.44105924624942
0.25 | 482.0 | 1.3101736972704714 | 629.0 | 2.029925187032419 | 616.0 | 1.949748743718593 | 70.6640336842167
0.3 | 440.0 | 1.1017369727047146 | 601.0 | 1.8902743142144638 | 627.0 | 2.0050251256281406 | 68.1900210987737
0.35 | 435.0 | 1.0769230769230769 | 593.0 | 1.8503740648379052 | 620.0 | 1.9698492462311559 | 67.46649907706849
0.4 | 468.0 | 1.2406947890818858 | 625.0 | 2.0099750623441395 | 632.0 | 2.030150753768844 | 70.31593287908903
0.45 | 451.0 | 1.1563275434243176 | 622.0 | 1.9950124688279303 | 640.0 | 2.07035175879397 | 70.05372214776233
0.5 | 461.0 | 1.205955334987593 | 617.0 | 1.9700748129675811 | 633.0 | 2.0351758793969847 | 69.61450952869981
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

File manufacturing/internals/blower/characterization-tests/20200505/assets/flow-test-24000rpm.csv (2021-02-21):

t | p1_adc | patient | p2_adc | p2 | p3_adc | p3 | Q1
0.019 | 518.0 | 1.488833746898263 | 757.0 | 2.6683291770573567 | 746.0 | 2.6030150753768844 | 81.0173643874324
0.038 | 534.0 | 1.5682382133995036 | 787.0 | 2.8179551122194515 | 801.0 | 2.879396984924623 | 83.25789831176792
0.057 | 530.0 | 1.5483870967741935 | 708.0 | 2.423940149625935 | 717.0 | 2.457286432160804 | 77.21814323012694
0.076 | 3.725320496528184e-09 | -1.0818858560609166 | 737.0 | 2.56857855361596 | 744.0 | 2.592964824120603 | 79.48859750271231
0.094 | 526.0 | 1.5285359801488834 | 713.0 | 2.4488778054862843 | 704.0 | 2.391959798994975 | 77.61433948532223
0.113 | 505.0 | 1.4243176178660049 | 682.0 | 2.29426433915212 | 676.0 | 2.251256281407035 | 75.12424764860722
0.132 | 474.0 | 1.2704714640198511 | 705.0 | 2.4089775561097255 | 732.0 | 2.5326633165829144 | 76.97944669850344
0.151 | 505.0 | 1.4243176178660049 | 751.0 | 2.638403990024938 | 761.0 | 2.678391959798995 | 80.56178046992667
0.17 | 539.0 | 1.5930521091811414 | 752.0 | 2.6433915211970076 | 758.0 | 2.663316582914573 | 80.63788986854473
0.189 | 522.0 | 1.5086848635235732 | 674.0 | 2.254364089775561 | 700.0 | 2.371859296482412 | 74.46812811555122
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

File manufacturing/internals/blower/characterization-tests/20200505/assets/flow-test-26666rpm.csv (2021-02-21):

t | p1_adc | patient | p2_adc | p2 | p3_adc | p3 | Q1
0.05 | 585.0 | 1.8213399503722085 | 838.0 | 3.0723192019950125 | 847.0 | 3.1105527638190953 | 86.93438295406521
0.15 | 618.0 | 1.9851116625310175 | 840.0 | 3.082294264339152 | 857.0 | 3.1608040201005023 | 87.0753958333687
0.2 | 559.0 | 1.6923076923076923 | 828.0 | 3.0224438902743143 | 850.0 | 3.1256281407035176 | 86.22585946185266
0.25 | 543.0 | 1.6129032258064515 | 835.0 | 3.057356608478803 | 840.0 | 3.0753768844221105 | 86.72243371644613
0.3 | 545.0 | 1.6228287841191067 | 744.0 | 2.603491271820449 | 736.0 | 2.5527638190954773 | 80.02698796478866
0.35 | 562.0 | 1.7071960297766748 | 847.0 | 3.117206982543641 | 848.0 | 3.1155778894472363 | 87.5671526847029
0.45 | 580.0 | 1.7965260545905708 | 826.0 | 3.0124688279301743 | 845.0 | 3.100502512562814 | 86.08345497249391
0.5 | 571.0 | 1.751861042183623 | 836.0 | 3.0623441396508726 | 845.0 | 3.100502512562814 | 86.79314097133647
0.55 | 574.0 | 1.7667493796526055 | 847.0 | 3.117206982543641 | 856.0 | 3.1557788944723617 | 87.5671526847029
0.6 | 559.0 | 1.6923076923076923 | 893.0 | 3.346633416458853 | 896.0 | 3.35678391959799 | 90.73241696209243
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

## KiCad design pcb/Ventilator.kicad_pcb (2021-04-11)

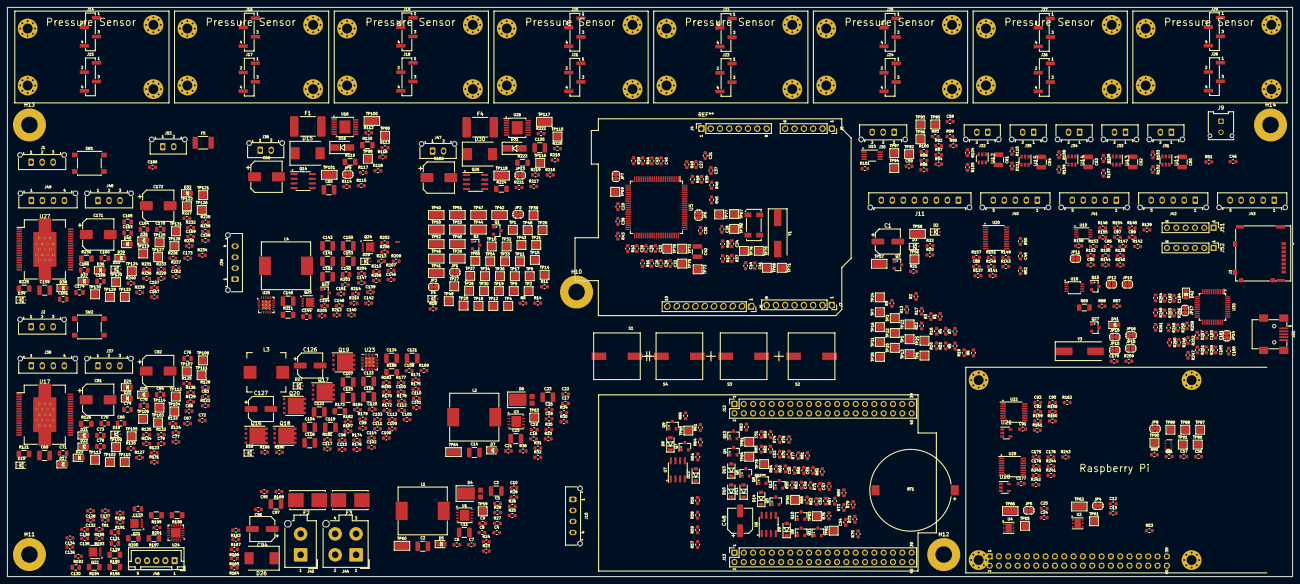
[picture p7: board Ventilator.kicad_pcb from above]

Board: 2 copper layers, 350.0 x 155.0 mm, 784 parts (1 on the bottom side), 430 nets, no tracks yet.

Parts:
BT1: CR2016; BatteryHolder_CR2016_MPD_BLP2016SM-G
C1, C48, C94, C126, C127: 33uF; CP_Elec_6.3x7.7
C2, C3, C14, C15, C42, C60, C61, C62, C63, C64, C65, C69, C97, C104, C107, C116, C118, C119, C121, C122, C123, C124, C125, C141, C143, C149, C150, C152, C153, C155, C159: 10uF; C_1210_3225Metric
C4, C8, C9, C16, C20, C21, C26, C32, C36, C37, C38, C39, C40, C41, C43, C45, C47, C50, C53, C56, C57, C58, C67, C68, C72, C77, C79, C85, C86, C87, C89, C90, C91, C92, C100, C101, C102, C111, C112, C113, C132, C138, C142, C146, C148, C157, C158, C162, C167, C169, C175, C176, C177, C181, C182, C183, C184, C185: 100nF; C_0603_1608Metric
C5, C17, C51, C52, C54, C55, C83, C95, C96, C103, C106, C117, C128, C134, C135, C136, C137, C173: 10nF; C_0603_1608Metric
C6, C18: 4.7nF; C_0603_1608Metric
C7, C19: 47pF; C_0603_1608Metric
C10, C12, C13, C22, C24, C25, C31, C35, C44, C46, C49, C59, C93, C105, C110, C151, C154, C178, C186: 1uF; C_0603_1608Metric
C11, C23: 47uF; C_1210_3225Metric
C27, C28: TBD; C_0603_1608Metric
C29, C30, C179, C180: 18pF; C_0603_1608Metric
C33, C34: 6.8pF; C_0603_1608Metric
C66, C81, C82, C156, C171, C172: 68uF; CP_Elec_8x10
C70, C71, C73, C74, C75, C76, C78, C80, C84, C144, C145, C160, C161, C163, C164, C165, C166, C168, C170, C174: 220nF; C_0805_2012Metric
C88: DNP; C_0603_1608Metric
C98: 1nF; C_0603_1608Metric
C99, C109: 47nF; C_0603_1608Metric
C108, C114, C115, C120, C140, C147: 100pF; C_0603_1608Metric
C129, C130, C131, C133: 470nF; C_0805_2012Metric
C139: 2.7nF; C_0603_1608Metric
D1, D2, D3, D18, D19, D27, D28, D29, D33, D34: BAT54J; D_SOD-323F
D4, D6: PDS760; D_PowerDI-5
D5, D7, D17, D32, D41: Green; LED_0805_2012Metric
D8: 2.0V; D_SOD-123
D9, D10: 3.3V; D_SOD-123
D11, D12, D13, D14: 1N4448W; D_SOD-123
D15, D26, D30: 20V; D_SMC
D16, D31: ES2B; D_SMA
D20, D21, D22, D23, D24, D25, D35, D36, D37, D38, D39, D40: Yellow; LED_0805_2012Metric
D42: Red; LED_0805_2012Metric
F1, F4: 2A; Fuse_2920_Bel_fuse
F2, F3: 10A; Fuseholder_Littelfuse_OMNI-BLOK-154
F5: 1.1A 16V; Fuse_1812_4532Metric_Castellated
H1: RaspberryPi
H2, H3, H4, H5, H6, H7, H8, H9: Pressure_sensor_daughterboard
H10, H11, H12, H13, H14: MountingHole_Pad; MountingHole_4.5mm_Pad
J1: Optical end stop 1; Molex_Micro-Fit_3.0_43650-0315_1x03_P3.00mm_Vertical
J2: Optical end stop 2; Molex_Micro-Fit_3.0_43650-0315_1x03_P3.00mm_Vertical
J3: 503182-1852; SD_Molex_5031821852
J4, J7: Arduino Connector; PinSocket_1x08_P2.54mm_Vertical
J5: Arduino Connector; PinSocket_1x06_P2.54mm_Vertical
J6: Arduino Connector; PinSocket_1x10_P2.54mm_Vertical
J8: Raspberry Pi; PinHeader_2x20_P2.54mm_Vertical
J9: Touchscreen power; Molex_Micro-Fit_3.0_43045-0212_2x01_P3.00mm_Vertical
J10: Alarm Battery (4x AA); Molex_Micro-Fit_3.0_43650-0415_1x04_P3.00mm_Vertical
J11: Cable to indicator board; Molex_Micro-Fit_3.0_43650-0815_1x08_P3.00mm_Vertical
J12: Mates J4 on BeMicro MAX10; PinSocket_2x20_P2.54mm_Vertical
J13: Mates J5 on BeMicro MAX10; PinSocket_2x20_P2.54mm_Vertical
J14, J15, J16, J17, J18, J19, J20, J21, J22, J23, J24, J25, J26, J27, J28, J29: Pressure sensor daughterboard; PinHeader_1x04_P2.54mm_Vertical_SMD_Pin1Right
J30: Oxygen sensor; Molex_Micro-Fit_3.0_43650-0315_1x03_P3.00mm_Vertical
J31, J32, J33, J34, J35: Temperature sensor (NTC); Molex_Micro-Fit_3.0_43650-0215_1x02_P3.00mm_Vertical
J36, J47: Solenoid; Molex_Micro-Fit_3.0_43650-0215_1x02_P3.00mm_Vertical
J37, J48: Limit switch; Molex_Micro-Fit_3.0_43650-0315_1x03_P3.00mm_Vertical
J38, J49: Stepper Motor Windings; Molex_Micro-Fit_3.0_43650-0415_1x04_P3.00mm_Vertical
J39: Molex Micro-Fit; Molex_Micro-Fit_3.0_43650-0415_1x04_P3.00mm_Vertical
J40, J41, J42, J43: Molex Micro-Fit; Molex_Micro-Fit_3.0_43650-0515_1x05_P3.00mm_Vertical
J44: POWER-ENTRY MegaFit 2x2; Molex_Mega-Fit_76829-0104_2x02_P5.70mm_Vertical
J45: BAT-PWR MegaFit 2x1; Molex_Mega-Fit_76829-0102_2x01_P5.70mm_Vertical
J46: BAT-BALANCE JST XH 5-pin; JST_XH_B5B-XH-A_1x05_P2.50mm_Vertical
J50: USB B micro; USB_Mini-B_Wuerth_65100516121_Horizontal
J51: Backup debug in for cycle controller; PinHeader_1x06_P2.54mm_Vertical
J52: Debug in for ST-LINK; PinHeader_1x06_P2.54mm_Vertical
J53: Fan; Molex_Micro-Fit_3.0_43650-0215_1x02_P3.00mm_Vertical
JP1, JP2, JP3, JP4, JP5, JP8, JP9, JP10, JP11, JP13, JP14, JP15, JP16, JP17, JP19: Jumper_NC_Small; SolderJumper-2_P1.3mm_Bridged_RoundedPad1.0x1.5mm
JP6: Jumper; SolderJumper-2_P1.3mm_Open_RoundedPad1.0x1.5mm
JP7: Jumper; SolderJumper-2_P1.3mm_Bridged_RoundedPad1.0x1.5mm
JP12, JP18: Jumper_NO_Small; SolderJumper-2_P1.3mm_Open_RoundedPad1.0x1.5mm
L1, L2: 15uH; L_TDK_SPM12565VT
L3: SRP1038A-3R3M; L_Bourns-SRP1038
L4: 6.8uH; L_TDK_SPM12565VT
NT1: Net-Tie_2; NetTie-2_SMD_Pad0.5mm
Q1, Q2, Q3, Q4, Q5, Q6, Q8, Q9, Q11, Q12, Q13, Q15, Q23, Q27: MMBT3904; SOT-23
Q7, Q10: MMBT2907A; SOT-23
Q14, Q26: FDS4672A; SOIC-8_3.9x4.9mm_P1.27mm
Q16, Q17, Q18, Q19: BSC065N06LS5ATMA1; VSONP-8-1EP_5x6_P1.27mm
Q20: SI7145DP-T1-GE3; VSONP-8-1EP_5x6_P1.27mm
Q21, Q22, Q24, Q25: BSZ019N03LSATMA1; VSON-8-SGD_3.3x3.3mm_P0.65mm_NexFET
R1, R2, R3, R4, R5, R6, R7, R8, R20, R21, R73, R74, R79, R80, R82, R83, R85, R86, R115, R125, R128, R131, R132, R133, R134, R135, R136, R139, R141, R189, R195, R219, R229, R232, R235, R236, R237, R238, R239, R240, R255, R256: 1k; R_0603_1608Metric
R9, R18, R19, R41, R87, R88, R142, R143, R144, R145, R146, R147, R148, R149, R150, R151, R152, R153, R253, R254: 4.7k; R_0603_1608Metric
R10, R11, R12, R13, R14, R15, R16, R17, R63, R66, R71, R72, R112, R170, R172, R176, R212, R216, R246, R257, R258: 100k; R_0603_1608Metric
R22, R39, R40, R42, R43, R45, R46, R47, R48, R49, R50, R51, R52, R53, R90, R91, R122, R123, R127, R140, R154, R155, R156, R157, R158, R177, R178, R184, R186, R226, R227, R231, R241, R248, R249: 0; R_0603_1608Metric
R23, R30, R171, R175: 316k; R_0603_1608Metric
R24, R27, R31, R34, R69, R114, R208, R218: 52.3k; R_0603_1608Metric
R25, R32, R70: 249k; R_0603_1608Metric
R26, R33: 16.9k; R_0603_1608Metric
R28, R35, R37, R44, R54, R55, R56, R57, R58, R59, R60, R61, R65, R68, R76, R81, R84, R92, R93, R94, R95, R96, R97, R98, R100, R113, R117, R137, R138, R160, R162, R181, R182, R185, R191, R202, R203, R204, R205, R207, R213, R215, R217, R221, R243, R245, R250, R261: 10k; R_0603_1608Metric
R29, R36, R64, R99, R118, R222: 2k; R_0603_1608Metric
R38, R192, R193, R252, R260: 100; R_0603_1608Metric
R62, R77, R78, R214: 1M; R_0603_1608Metric
R67, R163, R166, R169: 442k; R_0603_1608Metric
R75: 680; R_0603_1608Metric
R89, R119, R120, R121, R126, R223, R224, R225, R230: 0; R_1206_3216Metric
R101, R116, R220, R247: 1.5k; R_0603_1608Metric
R102, R104, R106, R108, R110: 220 0.1%; R_0603_1608Metric
R103, R105, R107, R109, R111: 10k 0.1%; R_0603_1608Metric
R124, R129, R130, R164, R165, R167, R168, R228, R233, R234, R251: 39k; R_0603_1608Metric
R159, R161, R242, R244, R259: DNP; R_0603_1608Metric
R173, R188, R194, R200: 0.01; R_1206_3216Metric
R174, R201, R209, R210: 10; R_0603_1608Metric
R179, R180: 4.02k; R_0603_1608Metric
R183: 3M; R_0603_1608Metric
R187: 30.1k; R_0603_1608Metric
R190: 2k; R_1206_3216Metric
R196, R197, R198, R199: 49.9; R_1206_3216Metric
R206: 6.49k; R_0603_1608Metric
R211: 0.006; R_1206_3216Metric
S1, S2, S3, S4: CT-1205H-SMT; CT-1205H-SMT-TR
SW1: User TBD; SW_Push_6x6
SW2: Reset CC; SW_Push_6x6
TH1: 10k; R_0603_1608Metric
TP1, TP2, TP3, TP4, TP5, TP6, TP10, TP11, TP12, TP13, TP14, TP15, TP16, TP17, TP23, TP24, TP25, TP26, TP27, TP28, TP29, TP30, TP31, TP32, TP33, TP34, TP56, TP80, TP81, TP82, TP83, TP84, TP85, TP97, TP98, TP99, TP115, TP116: TP; TestPoint_Pad_2.0x2.0mm
TP7: PG-12V; TestPoint_Pad_2.0x2.0mm
TP8: PMon-IBat; TestPoint_Pad_2.0x2.0mm
TP9: PMon-IAdp; TestPoint_Pad_2.0x2.0mm
TP18: Stepper-ADC-In1; TestPoint_Pad_2.0x2.0mm
TP19: Stepper-ADC-In2; TestPoint_Pad_2.0x2.0mm
TP20: UART-Rx-STM-Tx-STLink; TestPoint_Pad_2.0x2.0mm
TP21: UART-Tx-STM-Rx-STLink; TestPoint_Pad_2.0x2.0mm
TP22: FPGA-ADC-nInt; TestPoint_Pad_2.0x2.0mm
TP35: PSol-CS1; TestPoint_Pad_2.0x2.0mm
TP36: CC-SDA; TestPoint_Pad_2.0x2.0mm
TP37: Low-Alarm-Bat; TestPoint_Pad_2.0x2.0mm
TP38: CC-SCL; TestPoint_Pad_2.0x2.0mm
TP39, TP40, TP41, TP42, TP44, TP45, TP46, TP47, TP50, TP51, TP52, TP53, TP57, TP58, TP60, TP62, TP64, TP66, TP100, TP101, TP117, TP118: TestPoint_Flag; TestPoint_Keystone_5019_Minature
TP43: PSol-CS2; TestPoint_Pad_2.0x2.0mm
TP48: UART-RTS-STM-CTS-RPi; TestPoint_Pad_2.0x2.0mm
TP49: UART-CTS-STM-RTS-RPi; TestPoint_Pad_2.0x2.0mm
TP54: UART-Tx-RPi-Rx-STM; TestPoint_Pad_2.0x2.0mm
TP55: UART-Rx-RPi-Tx-STM; TestPoint_Pad_2.0x2.0mm
TP59, TP61, TP63, TP65: ~Power Good; TestPoint_Pad_2.0x2.0mm
TP67: SPI-MISO; TestPoint_Pad_2.0x2.0mm
TP68: SPI-MOSI; TestPoint_Pad_2.0x2.0mm
TP69: SPI-SCLK; TestPoint_Pad_2.0x2.0mm
TP70: uSD-nCS; TestPoint_Pad_2.0x2.0mm
TP71: PD3; TestPoint_Pad_2.0x2.0mm
TP72: PD4; TestPoint_Pad_2.0x2.0mm
TP73: PD5; TestPoint_Pad_2.0x2.0mm
TP74: PD6; TestPoint_Pad_2.0x2.0mm
TP75: PE0; TestPoint_Pad_2.0x2.0mm
TP76: PE1; TestPoint_Pad_2.0x2.0mm
TP77: PE2; TestPoint_Pad_2.0x2.0mm
TP78: PE3; TestPoint_Pad_2.0x2.0mm
TP79: PD-Alarm; TestPoint_Pad_2.0x2.0mm
TP86: Inh-Flow; TestPoint_Pad_2.0x2.0mm
TP87: Exh-Flow; TestPoint_Pad_2.0x2.0mm
TP88: Oxy-Flow; TestPoint_Pad_2.0x2.0mm
TP89: Oxy-Pressure; TestPoint_Pad_2.0x2.0mm
TP90: Mix-Tank-Pressure; TestPoint_Pad_2.0x2.0mm
TP91: Patient-Pressure; TestPoint_Pad_2.0x2.0mm
TP92: Stepper1-Temp; TestPoint_Pad_2.0x2.0mm
TP93: Stepper2-Temp; TestPoint_Pad_2.0x2.0mm
TP94: Blower-Temp; TestPoint_Pad_2.0x2.0mm
TP95: Batt-Temp; TestPoint_Pad_2.0x2.0mm
TP96: Spare-Temp; TestPoint_Pad_2.0x2.0mm
TP102, TP119: nCS; TestPoint_Pad_2.0x2.0mm
TP103, TP120: StCk; TestPoint_Pad_2.0x2.0mm
TP104, TP121: SDI; TestPoint_Pad_2.0x2.0mm
TP105, TP122: CK; TestPoint_Pad_2.0x2.0mm
TP106, TP123: OscIn; TestPoint_Pad_2.0x2.0mm
TP107, TP124: OscOut; TestPoint_Pad_2.0x2.0mm
TP108, TP125: SDO; TestPoint_Pad_2.0x2.0mm
TP109, TP126: nBusy-Sync; TestPoint_Pad_2.0x2.0mm
TP110, TP127: nFlag; TestPoint_Pad_2.0x2.0mm
TP111, TP128: Out-A1; TestPoint_Pad_2.0x2.0mm
TP112, TP129: Out-A2; TestPoint_Pad_2.0x2.0mm
TP113, TP130: Out-B1; TestPoint_Pad_2.0x2.0mm
TP114, TP131: Out-B2; TestPoint_Pad_2.0x2.0mm
U1, U3: TPS54561; WSON-10-1EP_4x4mm_P0.8mm_EP2.6x3mm
U2, U4: LD39050PU33R; DFN-6-1EP_3x3mm_P0.95mm_EP1.75x2.5mm
U5: STM32L496VGT; LQFP-100_14x14mm_P0.5mm
U6, U7: TLC555; SOIC-8_3.9x4.9mm_P1.27mm
U8: TL431LI; SOT-23
U9: BMP280; Bosch_BMP280
U10: INA333AIDGKR; VSSOP-8_3.0x3.0mm_P0.65mm
U11, U12, U13, U14, U15: USBLC6-2SC6; SOT-23-6
U16, U26: TPS1H100A; TSSOP-14-1EP_4.4x5mm_P0.65mm
U17, U27: L6470PD; ST_POWERSO36_ThermalVias
U18: 24LC256T-I_MS; TSSOP-8_3x3mm_P0.65mm
U19: SN74LVC2T45DCTR; SSOP-8_2.95x2.8mm_P0.65mm
U20: TCA9544APWR; TSSOP-20_4.4x6.5mm_P0.65mm
U21, U28: LM4120-IM5X-3.3; SOT-23-5
U22, U29: ADC128D818; TSSOP-16_4.4x5mm_P0.65mm
U23: BQ24773; QFN-28-1EP_4x4mm_P0.4mm_EP2.6x2.6mm_ThermalVias
U24: MAX17320G20+; WQFN-24-1EP_4x4mm_P0.5mm_EP2.6x2.6mm
U25: LM5141; VQFN-24-1EP_4x4mm_P0.5mm_EP2.45x2.45mm_ThermalVias
U30: STM32F103CBT6; LQFP-48_7x7mm_P0.5mm
Y1, Y3: 8 Mhz; Crystal_SMD_HC49-SD
Y2: 32.768 kHz; Crystal_SMD_Abracon_ABS25

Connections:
+3.3V_Ctrl: C13.2, C31.1, C32.1, C38.1, C39.1, C40.1, C41.1, C42.1, C69.1, C77.1, C79.2, C85.2, C86.2, C89.2, C92.2, C93.2, C159.1, C167.1, C169.2, C182.2, C183.2, C184.2, C185.2, D1.1, D8.1, J3.4, J4.2, J4.4, J51.1, J52.1, JP3.1, JP6.2, JP10.1, JP18.1, Q27.2, R5.2, R9.1, R18.1, R19.1, R37.1, R41.2, R113.1, R121.2, R124.2, R127.2, R128.1, R129.2, R130.2, R132.2, R133.2, R142.1, R143.1, R144.1, R145.1, R146.1, R147.1, R148.1, R149.1, R150.1, R151.1, R152.1, R153.1, R154.2, R155.2, R156.2, R157.2, R158.2, R159.2, R161.2, R181.2, R185.1, R215.1, R217.1, R225.2, R228.2, R231.2, R232.1, R233.2, R234.2, R236.2, R237.2, R253.2, R255.1, R258.1, TP62.1, U2.4, U5.11, U5.28, U5.50, U5.73, U5.75, U5.100, U16.12, U17.9, U17.24, U18.8, U19.1, U19.5, U20.20, U22.5, U26.12, U27.9, U27.24, U30.1, U30.9, U30.24, U30.36, U30.48
+3.3V_FPGA: C177.2, C178.2, J12.1, J12.2, J13.29, R87.1, R88.1, R241.2, R242.2, R244.2, U29.5
+3.3V_Sns: C25.2, C43.1, C44.1, C56.2, C57.2, C58.2, J14.3, J16.3, J18.3, J20.3, J22.3, J24.3, J26.3, J28.3, R45.2, R93.2, R95.2, R102.2, R104.2, R106.2, R108.2, R110.2, TP66.1, U4.4, U5.22, U9.2, U9.6, U9.8, U10.7, U11.5, U12.5, U13.5, U14.5, U15.5
+3V3_Rpi: J8.1, J8.17, R50.1, R52.1
+5V: C21.2, C22.2, C23.2, C24.2, C90.2, C175.2, D2.2, D9.1, D10.1, D11.2, J1.1, J4.5, J4.8, J11.2, JP5.2, JP11.1, L2.2, R22.1, R34.1, R36.1, R89.2, S2.1, S3.1, TP64.1, U4.6, U21.3, U21.4, U28.3, U28.4
+5V_GUI: C9.2, C10.2, C11.2, C45.1, C46.1, J8.2, J8.4, J9.2, L1.2, R27.1, R29.1, S4.1, TP60.1
+5V_Sns: C1.1, J14.1, J16.1, J18.1, J20.1, J22.1, J24.1, J26.1, J28.1, R22.2, TP58.1
+5V_USB: D3.2, J50.1, R250.2
+12V: C147.2, C149.1, C150.1, C152.1, C153.1, C186.1, F5.2, R126.2, R211.1, R212.1, R214.1, R230.2, U25.17
+12V_Step1: C70.1, C71.1, C73.1, C74.1, C75.1, C76.1, C78.1, C80.1, C81.1, C82.1, C84.1, C160.1, C161.1, C163.1, C164.1, C165.1, C166.1, C168.1, C170.1, C171.1, C172.1, C174.1, D18.2, D33.2, R122.2, R126.1, R226.2, R230.1, U17.4, U17.5, U17.15, U17.16, U17.22, U17.23, U17.33, U17.34, U27.4, U27.5, U27.15, U27.16, U27.22, U27.23, U27.33, U27.34
+BATT: C48.1, C50.2, C53.2, D11.1, Q7.2, Q10.3, R56.2, R61.2, R66.2, R69.2, R75.2, S1.1, U6.8, U7.8
+VLink: C2.1, C3.1, C4.2, C14.1, C15.1, C16.2, C65.1, C66.1, C141.1, C143.1, C155.1, C156.1, J44.3, Q24.3, R23.1, R30.1, R120.1, R207.1, R224.1, U1.2, U3.2, U16.8, U16.9, U16.10, U25.15, U26.8, U26.9, U26.10
/Add'l aux functions/Blower-Enable: JP3.2, R139.2
/Alarms and Power Monitoring/Alarm-Bat: D14.2, J10.1, R71.1
/Alarms and Power Monitoring/Low-Alarm-Bat: Q10.2, R78.1, R81.1, R84.1, TP37.1, TP84.1
/Alarms and Power Monitoring/PD-Alarm: C47.2, D12.1, D13.1, R63.2, TP79.1, U6.4
/Aux-I2C-Switch-nINT: JP2.2, U20.17
/Bat-Alert: R3.1, U5.77, U24.7
/Blower-Ctrl: R137.1, U5.63, U19.2
/CC-Buzzer: J7.6, R79.1, TP82.1, U5.53
/CC-LED-G: J5.3, J11.3, U5.67
/CC-LED-R: J11.4, U5.65
/CC-LED-Y: J11.5, U5.66
/CC-SCL: J6.10, J15.4, J17.4, J19.4, J21.4, J23.4, J25.4, J27.4, J29.4, R19.2, R91.1, TP38.1, U5.95, U18.6, U20.18, U22.3, U23.12, U24.8
/CC-SDA: J6.9, J15.3, J17.3, J19.3, J21.3, J23.3, J25.3, J27.3, J29.3, R18.2, R90.1, TP36.1, U5.96, U18.5, U20.19, U22.2, U23.11, U24.9
/CC-Stepper-Reset: J7.3, R4.1, U5.48
/Cycle Controller/BOOT0: R44.2, U5.94
/Cycle Controller/PH0: JP1.1, JP2.1, R9.2, R42.1, U5.12
/Cycle Controller/RTC-Batt: BT1.1, C35.1, JP6.1, U5.6
/Cycle Controller/Stepper-Lim-Sw1: C27.2, R39.1, U5.78
/Cycle Controller/Stepper-Lim-Sw2: C28.2, R40.1, U5.79
/Cycle Controller/uSD-Detect: J3.Detect, R37.2, U5.64
/Cycle Controller/uSD-nCS: J3.2, TP70.1, U5.29
/Exh-Flow: J17.1, R10.2, TP87.1, U5.33
/FPGA's ADC/ADC0: R10.1, U29.16
/FPGA's ADC/ADC1: R11.1, U29.15
/FPGA's ADC/ADC2: R12.1, U29.14
/FPGA's ADC/ADC3: R13.1, U29.13
/FPGA's ADC/ADC4: R14.1, U29.12
/FPGA's ADC/ADC5: R15.1, U29.11
/FPGA's ADC/ADC6: R16.1, U29.10
/FPGA's ADC/ADC7: R17.1, U29.9
/FPGA's ADC/nINT: TP22.1, U29.6
/FPGA-Buzzer: J13.1, R82.1, TP83.1
/FPGA-Stepper-Reset: J13.7, R6.2
/GUI-Buzzer: J8.32, R85.1, TP85.1
/Inh-Flow: J5.2, J15.1, R12.2, TP86.1, U5.24
/Logic/Control Power Supplies/3.3V Logic Supply/In: C12.2, D2.1, D3.1, JP4.2, TP57.1, U2.6
/Logic/Control Power Supplies/5V Control Supply/Fb: R34.2, R35.1, U3.6
/Logic/Control Power Supplies/5V Control Supply/nEnable: R30.2, R31.1, U3.3
/Logic/Control Power Supplies/5V UI Supply/Fb: R27.2, R28.1, U1.6
/Logic/Control Power Supplies/5V UI Supply/nEnable: Q3.2, R23.2, R24.1, U1.3
/Low-Alarm-Bat: D1.2, R2.1, R84.2
/Mix-Tank-Pressure: J21.1, TP90.1, U5.17
/Oxygen-FiO2: C59.2, J5.6, R13.2, R101.2, TP97.1, U5.15
/Oxygen-Flow: J19.1, R11.2, TP88.1, U5.34
/Oxygen-Pressure: J25.1, R16.2, TP89.1, U5.18
/PMon-ACOK: J5.4, R185.2, U5.92, U23.5
/PMon-PSys: C114.1, R187.1, U22.11, U23.9
/PSol1-Ctrl: J6.1, R219.2, TP115.1, U5.47, U26.3
/PSol1-nFault: JP13.1, R217.2, U5.93
/PSol2-Ctrl: R115.2, TP98.1, U5.23, U16.3
/PSol2-nFault: JP9.1, R43.1, R113.2, U5.13
/PSol Driver, Spare/CS: R112.1, R114.1, TP43.1
/PSol Driver/CS: R216.1, R218.1, TP35.1
/Patient-Pressure: J5.5, J23.1, R14.2, TP91.1, U5.16
/Power Entry / Battery Handling/12V System Buck Converter/LM5141-AGND: C140.2, C142.1, C144.1, C145.1, C148.2, NT1.1, R204.2, R206.2, R208.2, U25.3, U25.6
/Power Entry / Battery Handling/12V System Buck Converter/LM5141-VCC: C151.2, C154.2, D29.2, U25.10
/Power Entry / Battery Handling/12V System Buck Converter/LM5141-VDDA: C148.1, R203.1, U25.2
/Power Entry / Battery Handling/Bat-N: C97.2, C128.2, C129.2, C130.2, C131.2, C135.2, C138.2, J45.1, R191.2, R194.1, R195.2, R200.1, TH1.2, U24.15, U24.20, U24.25
/Power Entry / Battery Handling/Bat-P: C97.1, C132.1, F3.2, Q22.1, R201.1
/Power Entry / Battery Handling/Battery Charger / Source Switching/Pack-P: D27.2, Q20.3, Q21.1, R166.1, R175.1, R189.1, R190.2, U23.17
/Power Entry / Battery Handling/Battery Charger / Source Switching/RegN: C110.1, R171.1, R182.2, U23.24
/Power Entry / Battery Handling/Battery Charger / Source Switching/VIn-Adp: C98.1, Q16.3, R169.1
/Power Entry / Battery Handling/PG-12V: R215.2, TP7.1, U25.21
/Power Entry / Battery Handling/PMon-IAdp: C120.1, TP9.1, U23.7
/Power Entry / Battery Handling/PMon-IBat: C115.1, TP8.1, U23.8
/Power Entry / Battery Handling/Power-Sw-P: C111.1, C113.1, C116.1, C117.1, C118.1, C119.1, C121.1, C122.1, C123.1, C124.1, C125.1, C126.1, C127.1, J44.4, L3.2, R188.2, U23.20
/Power Entry / Battery Handling/Vin-Adp: C94.1, D26.1, F2.1, R163.1
/STM Programmer for cycle controller/CC-SWCLK: J51.2, JP14.1, U5.76
/STM Programmer for cycle controller/CC-SWCLK-Out: JP14.2, U30.15, U30.26
/STM Programmer for cycle controller/CC-SWDIO: J51.4, JP15.1, U5.72
/STM Programmer for cycle controller/CC-SWDIO-Out: JP15.2, R260.2, U30.27
/STM Programmer for cycle controller/CC-SWO: J51.6, JP17.1, U5.89
/STM Programmer for cycle controller/CC-SWO-Out: JP17.2, U30.31
/STM Programmer for cycle controller/CC-nRST: C37.1, J4.3, J51.5, JP16.1, SW2.1, U5.14
/STM Programmer for cycle controller/CC-nRST-Out: JP16.2, U30.18
/STM Programmer for cycle controller/Prog-SWCLK: J52.2, U30.37
/STM Programmer for cycle controller/Prog-SWDIO: J52.4, U30.34
/STM Programmer for cycle controller/Prog-nRST: C181.2, J52.5, R258.2, U30.7
/STM Programmer for cycle controller/USB-D+: R248.1, U30.33
/STM Programmer for cycle controller/USB-D-: R249.2, U30.32
/STM Programmer for cycle controller/VSense: R253.1, R254.2, U30.10
/STM Programmer for cycle controller/nRenum-USB: R252.1, U30.38
/Safety FPGA/DIFF-RX-7+: J13.23, TP31.1
/Safety FPGA/DIFF-RX-7-: J13.24, TP32.1
/Safety FPGA/DIFF-RX-8+: J13.21, TP29.1
/Safety FPGA/DIFF-RX-8-: J13.22, TP30.1
/Safety FPGA/DIFF-RX-9+: J13.19, TP27.1
/Safety FPGA/DIFF-RX-9-: J13.20, TP28.1
/Safety FPGA/DIFF-RX-A+: J13.17, TP25.1
/Safety FPGA/DIFF-RX-A-: J13.18, TP26.1
/Safety FPGA/DIFF-RX-B+: J13.15, TP23.1
/Safety FPGA/DIFF-RX-B-: J13.16, TP24.1
/Safety FPGA/GPIO-11: J13.13, TP33.1
/Safety FPGA/GPIO-12: J13.14, TP34.1
/Safety FPGA/I2C-SCL-FPGA: J12.4, R88.2, U29.3
/Safety FPGA/I2C-SDA-FPGA: J12.3, R87.2, U29.2
/Stepper1-StCk: R124.1, TP103.1, U5.35, U17.32
/Stepper1-nBusy: D22.1, J6.3, R129.1, TP109.1, U5.51, U17.29
/Stepper2-StCk: J7.8, R228.1, TP120.1, U5.36, U27.32
/Stepper2-nBusy: D37.1, J6.2, R233.1, TP126.1, U5.52, U27.29
/Stepper Motor Driver (..)/ADC-In: C157.2, R226.1, R227.2, TP19.1, U27.8
/Stepper Motor Driver (..)/Out-A1: D40.2, J49.1, TP128.1, U27.2, U27.3
/Stepper Motor Driver (..)/Out-A2: D39.2, J49.2, TP129.1, U27.35, U27.36
/Stepper Motor Driver (..)/Out-B1: D38.2, J49.3, TP130.1, U27.17, U27.18
/Stepper Motor Driver (..)/Out-B2: D36.2, J49.4, TP131.1, U27.20, U27.21
/Stepper Motor Driver (..)/SDI: TP108.1, TP121.1, U17.25, U27.27
/Stepper Motor Driver (..)/Switch: R229.1, R231.1, U27.7
/Stepper Motor Driver (...)/ADC-In: C67.2, R122.1, R123.2, TP18.1, U17.8
/Stepper Motor Driver (...)/Out-A1: D25.2, J38.1, TP111.1, U17.2, U17.3
/Stepper Motor Driver (...)/Out-A2: D24.2, J38.2, TP112.1, U17.35, U17.36
/Stepper Motor Driver (...)/Out-B1: D23.2, J38.3, TP113.1, U17.17, U17.18
/Stepper Motor Driver (...)/Out-B2: D21.2, J38.4, TP114.1, U17.20, U17.21
/Stepper Motor Driver (...)/Switch: R125.1, R127.1, U17.7
/Stepper-MISO: J3.7, TP67.1, TP125.1, U5.31, U27.25
/Stepper-MOSI: J3.3, TP68.1, TP104.1, U5.32, U17.27
/Stepper-SCK: J3.5, TP69.1, TP105.1, TP122.1, U5.30, U17.26, U27.26
/Stepper-nCS: J7.5, TP102.1, TP119.1, U5.54, U17.30, U27.30
/Stepper-nFlag: D20.1, D35.1, J7.4, R130.1, R234.1, TP110.1, TP127.1, U5.37, U17.31, U27.31
/Stepper-nReset: C72.2, C162.2, Q1.2, Q2.2, R5.1, U17.6, U27.6
/SysMonADC-nINT: JP1.2, U22.6
/System Monitor ADC/ADC0: C60.1, R103.2, TP92.1, U11.4, U22.16
/System Monitor ADC/ADC1: C61.1, R105.2, TP93.1, U12.4, U22.15
/System Monitor ADC/ADC2: C62.1, R107.2, TP94.1, U13.4, U22.14
/System Monitor ADC/ADC3: C63.1, R109.2, TP95.1, U14.4, U22.13
/System Monitor ADC/ADC4: C64.1, R111.2, TP96.1, U15.4, U22.12
/UART-CTS-RPi-RTS-STM: J8.36, U5.71
/UART-CTS-STM-RTS-FPGA: J13.9, U5.91
/UART-RTS-RPi-CTS-STM: R1.1, U5.70
/UART-RTS-STM-CTS-FPGA: J13.8, U5.90
/UART-Rx-FPGA-Tx-RPi: J8.24, J13.5
/UART-Rx-RPi-Tx-STM: J7.2, J8.10, TP55.1, U5.68
/UART-Rx-STM-Tx-FPGA: J13.3, U5.83
/UART-Rx-STM-Tx-STLink: TP20.1, U5.26, U30.12
/UART-Tx-FPGA-Rx-RPi: J13.6, R7.2
/UART-Tx-RPi-Rx-STM: J7.1, R8.2, TP54.1, U5.69
/UART-Tx-STM-Rx-FPGA: J13.4, U5.80
/UART-Tx-STM-Rx-STLink: J7.7, TP21.1, U5.25, U30.13
/UI Computer/GPIO0(ID_SD): J8.27, TP10.1
/UI Computer/GPIO1(ID_SC): J8.28, TP11.1
/UI Computer/GPIO2(SDA): J8.3, TP12.1
/UI Computer/GPIO3(SCL): J8.5, TP13.1
/UI Computer/GPIO7(CE1): J8.26, TP14.1
/UI Computer/GPIO9(MISO): J8.21, R7.1
/UI Computer/GPIO10(MOSI): J8.19, TP15.1
/UI Computer/GPIO11(SCLK): J8.23, TP16.1
/UI Computer/GPIO13(PWM1): J8.33, TP17.1
/UI Computer/GPIO14(TXD): J8.8, R8.1
/UI Computer/GPIO17: J8.11, R1.2
/UI Computer/GPIO18(PCM_CLK): J8.12, R2.2
/UI Computer/GPIO19(PCM_FS): J8.35, R3.2
/UI Computer/GPIO20(PCM_DIN): J8.38, TP1.1
/UI Computer/GPIO21(PCM_DOUT): J8.40, TP2.1
/UI Computer/GPIO22: J8.15, TP3.1
/UI Computer/GPIO23: J8.16, TP4.1
/UI Computer/GPIO24: J8.18, TP5.1
/UI Computer/GPIO27: J8.13, TP6.1
/UI Computer/UI_ID0: J8.22, R52.2, R53.1
/UI Computer/UI_ID1: J8.37, R50.2, R51.1
/UI-LED-G: J8.7, J11.6
/UI-LED-R: J8.29, J11.7
/UI-LED-Y: J8.31, J11.8
/UI-Power-Off: J13.2, R20.1, R21.1, TP56.1
/VBat-Sense: C96.1, R166.2, R167.1, U22.10
/VSys-Power-Off: J13.10, R202.2
/Vin-Sense: C95.1, R17.2, R163.2, R164.1, U22.9
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

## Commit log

2021-02-07 Deploying to gh-pages from @ 1c547261536b6b985854beaf175ef62d2daa9604 🚀
2021-02-07 Deploying to gh-pages from @ 15ca014c2c9f129bd82f7ff4c72c19f20ca37816 🚀
2021-02-08 Deploying to gh-pages from @ e14e7703ffb0aee3341f4c2af8b4841c50042f70 🚀
2021-02-08 Deploying to gh-pages from @ b7e3fbd7a4c2e836c715aa10a18925a85b992dc2 🚀
2021-02-12 Deploying to gh-pages from @ 8a858f846f7070da52a3a887d7d8483895f6ccf8 🚀
2021-02-12 Deploying to gh-pages from @ 8368e4d681a645716ed333cff655b5ee0bba68a6 🚀
2021-02-17 Deploying to gh-pages from @ ae72c093d44523a3d913cbf50dd8bca295ead8b8 🚀
2021-02-17 Deploying to gh-pages from @ 20a77098c256f37946fb119cd40c5674ba4c1cd8 🚀
2021-04-12 WIP - generate BOM
    [BOM_raw.csv]

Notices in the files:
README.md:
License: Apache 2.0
